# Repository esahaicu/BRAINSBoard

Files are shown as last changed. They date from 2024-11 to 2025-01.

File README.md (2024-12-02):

# BRAINSBoard

<p align="center">
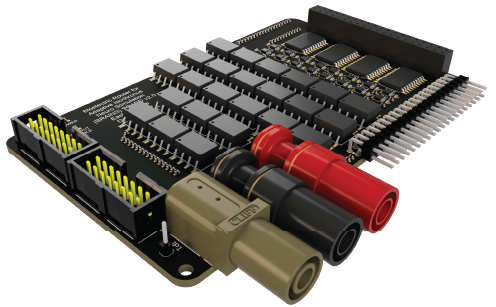
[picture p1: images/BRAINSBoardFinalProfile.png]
 
</p>

# Abstract

  **Objective:** Multipolar Intracranial Electrical Brain Stimulation (ICBS) is a promising method increasingly explored for use in both closed-loop neuromodulation experiments and clinical treatments for neurological diseases. Current tools for multipolar ICBS face several limitations that hinder exploratory research: high entry costs, lack of flexibility in managing different stimulation parameters and electrodes, absence of an open-source, customizable platform, and often an overabundance of features unnecessary for single-unit level exploratory research. These constraints limit the progress in understanding and applying multipolar ICBS effectively. To address these challenges, we developed the Bioelectric Router for Adaptive Isochronous Neuro Stimulation (BRAINS) Board.

  **Approach:** The BRAINS Board a cost-effective and customizable device designed to facilitate multipolar stimulation experiments across a 16-channel electrode array using common research electrode setups. The BRAINS Board interfaces with a microcontroller, allowing users to configure each channel for cathodal or anodal input, establish a grounded connection, or maintain a floating state. The design prioritizes ease of integration by leveraging standard tools like a microcontroller and an Analog Isolated Stimulator while providing options to customize setups according to experimental conditions. It also ensures output isolation, reduces noise, and supports remote configuration changes for rapid switching of electrode states. To test the efficacy of the board, there will be a series of tests run with 2 different stimulators with a fixed set of currents congruent with typical microcurrent brain stimulation. There will be 2 sets of bench tests: first with a direct connection to a DAQ system with current passing through 110KΩ resistors for all channels; next, a test through stimulation sent through contacts of a 16 channel electrode in saline and recordings through a Neuropixel. Once completed, monopolar, bipolar, and multipolar parameters will be tested in-vivo with stimulation and 3 Neuropixel recordings in V1.

  **Main Results:** The BRAINS Board, when delivering stimulation through a conventional isolated stimulator (A-M 4100), demonstrates no significant differences in Root Mean Square Error (RMSE) noise or signal-to-noise ratio compared to the baseline performance of the isolated stimulator alone. The board supports configuration changes at a rate of up to 600 Hz without introducing residual noise, enabling high-frequency switching necessary for temporally multiplexed multipolar stimulation.

  **Significance:** The BRAINS Board represents a significant advancement in exploratory brain stimulation research by providing a user-friendly, customizable, open source, and cost-effective tool capable of conducting sophisticated, reproducible, and finely controlled stimulation experiments. With its capacity for real-time information processing and efficient parameter exploration, the BRAINS Board is poised to enhance both exploratory research and clinical applications of closed-loop ICBS.

# Introduction

Intracranial electrical brain stimulation (EBS) is a cornerstone therapeutic approach in clinical neurology and neurosurgery, particularly for treating conditions like Parkinson's disease, obsessive compulsive disorder[1], [2], dystonia[3], and epilepsy[4]. Furthermore, microstimulation paradigms have been used for decades in animal research. Utilizing EBS with neural prosthetics has promise to improve the quality and efficacy of brain-machine interfaces[5]. Despite widespread clinical use and role in neuroscience research, our fundamental understanding of how EBS affects neural circuits remains surprisingly limited. Current clinical protocols rely heavily on trial-and-error programming approaches during and after electrode implantation stimulation parameters frequently require adjustment over multiple clinical visits to achieve optimal therapeutic effects [6], [7], [8].

While we know that EBS can activate varied neural elements - including somas, dendrites, and axons - the precise composition of recruited neural ensembles remains unclear[6], [7]. This knowledge gap is particularly evident in clinical settings, where stimulation parameters must often be modified empirically by clinicians during patient follow-up visits[8]. Recent advances in multipolar brain stimulation have shown promise [9] in providing more precise [10], [11] and efficient therapeutic outcomes [12]. Current FDA-approved devices typically offer unipolar, bipolar, and limited multipolar stimulation options (4-8 contacts), with clinicians generally exhausting unipolar configurations before exploring more complex stimulation patterns[6]. Research devices with more contacts....reference specific papers... However, investigating  advanced approaches, including multipolar stimulation, faces significant technical and practical barriers in most research settings. Traditional research tools for exploring multipolar stimulation, such as clinical neurostimulators or high-end research systems (e.g., Tucker-Davies STG5 Satellite, Intan headstages), are either prohibitively expensive, inflexible in their configuration, or excessive in their complexity for basic research applications [13].

The scientific community currently lacks access to flexible, open-source, cost-effective tools for exploring multipolar stimulation paradigms. Existing solutions often require substantial financial investment, offer limited customization options, and frequently include unnecessary features that complicate their use in fundamental research settings. These limitations have created a significant barrier to entry for researchers interested in exploring novel stimulation paradigms and understanding the basic principles of neural activation patterns.

To address these challenges, we developed a modular and readily reprogrammable interface - the Bioelectric Router for Adaptive Isochronous Neuro Stimulation (BRAINS) Board for control of electrical brain stimulation. This system enables rapid switching and multipolar stimulation while maintaining compatibility with existing monopolar and bipolar stimulation experimental frameworks. Our approach prioritizes accessibility, flexibility, and signal isolation while keeping costs aligned with standard experimental setups.   

# Hardware

The BRAINSBoard uses a custom designed PCB to ensure that:
 1) Output signal to the electrode array remains **isolated** with little to no leak or loss of current
 2) Channels can be set and changed **rapidly (~600Hz)**
 3) Channels can be controlled using any microcontroller and can be customizable

The BRAINSBoard is easy to plug into many up to 16-channel stimulation setups for experiments and can customizably recieve and communicate information to and from other devices in a setup. A current setup looks like:

<p align="center">
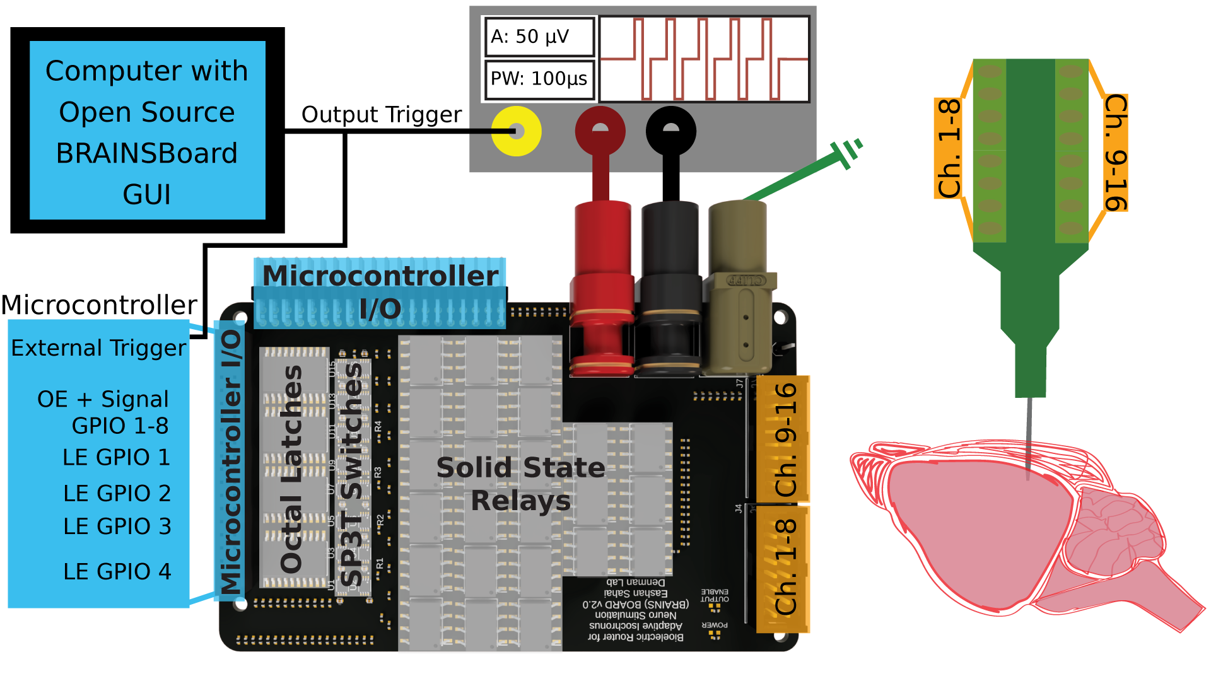
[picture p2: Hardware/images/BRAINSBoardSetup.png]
 
</p>

If you want to BUILD YOUR OWN:
Use the <a href="/Hardware/BRAINSBoard%20Production%20Files">following folder</a>, which has everything required to submit the PCB to a manufacturer to be processed.

For a more in-depth explanation of the schematic and setup of this board, <a href="/Hardware">look here</a>!

# Software

We have designed this to be compatible and easily programmed by any microcontroller. We have prewritten code to pair with an Arduino Pro Micro with the following configuration:

<p align="center">
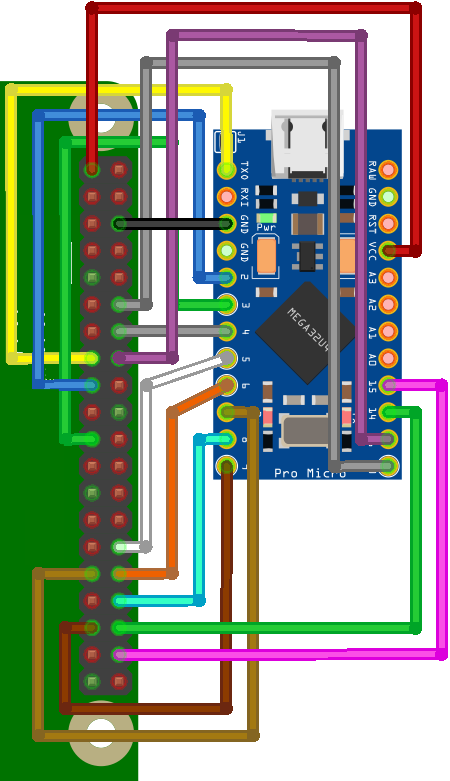
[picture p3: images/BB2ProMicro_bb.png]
 
</p>

Use the <a href="/Software/arduinoProMicroBRAINSBoard">following folder</a>, which has code that can be downloaded onto an Arduino Pro Micro.

The guide and description on how to easily control the board is <a href="/Software">here</a>!

# General Results

Hey! General results that will be good to prominently display as well as maybe setup pics could be great!

# Future Directions

Look forward <a href=https://github.com/esahaicu/BRAINSBoard/>HERE</a> for more updates on the BRAINSBoard that are based on, but not limited to, the following key improvements and a future timeline:

### By January 2025 - BRAINSBoard V3

1. Switching the <a href="https://cdn1-originals.webdamdb.com/14154_151801265?cache=1732603283&response-content-disposition=inline;filename=PAA193.pdf&response-content-type=application/pdf&Policy=eyJTdGF0ZW1lbnQiOlt7IlJlc291cmNlIjoiaHR0cCo6Ly9jZG4xLW9yaWdpbmFscy53ZWJkYW1kYi5jb20vMTQxNTRfMTUxODAxMjY1P2NhY2hlPTE3MzI2MDMyODMmcmVzcG9uc2UtY29udGVudC1kaXNwb3NpdGlvbj1pbmxpbmU7ZmlsZW5hbWU9UEFBMTkzLnBkZiZyZXNwb25zZS1jb250ZW50LXR5cGU9YXBwbGljYXRpb24vcGRmIiwiQ29uZGl0aW9uIjp7IkRhdGVMZXNzVGhhbiI6eyJBV1M6RXBvY2hUaW1lIjoyMTQ3NDE0NDAwfX19XX0_&Signature=KEhrRK-vYwk0ggFpEj8wrtBzJmtt7BLaQpuE0VpQ6zIkfrLoIbx35HtgxQp~mzP1G8wXjwMnEd2zExPyTWqPD8bcKLJTfQP483ssKtQgMZSv9g4kMZWmTeWzq72~uDpBGg3QDFOSoxpoQ4pNKS8JEbIiLR73WmyYWHy~x8HXiKn1oemtWMO5ZJkIW832eBlLtIbZF6mad9GiruNMyseB5M5vAtnD5xpdgm85AQOtLEowx-~A6fRC1GCmJKfGsC2NgjsDT588YpRlWTskNJhZ7zaYhGDO9GeALtxS0ZmNQy8JBUkahIwGCS4s0QiuV7Lvj7qD-rCDa4SswuSvqyvkgw__&Key-Pair-Id=APKAI2ASI2IOLRFF2RHA">current Solid State Relay</a> to a <a href="https://cdn1-originals.webdamdb.com/12956_135154079?cache=1729648393&response-content-disposition=inline;filename=OAA160.pdf&response-content-type=application/pdf&Policy=eyJTdGF0ZW1lbnQiOlt7IlJlc291cmNlIjoiaHR0cCo6Ly9jZG4xLW9yaWdpbmFscy53ZWJkYW1kYi5jb20vMTI5NTZfMTM1MTU0MDc5P2NhY2hlPTE3Mjk2NDgzOTMmcmVzcG9uc2UtY29udGVudC1kaXNwb3NpdGlvbj1pbmxpbmU7ZmlsZW5hbWU9T0FBMTYwLnBkZiZyZXNwb25zZS1jb250ZW50LXR5cGU9YXBwbGljYXRpb24vcGRmIiwiQ29uZGl0aW9uIjp7IkRhdGVMZXNzVGhhbiI6eyJBV1M6RXBvY2hUaW1lIjoyMTQ3NDE0NDAwfX19XX0_&Signature=AXHYEUwQeGlJv0wT-6YeKM1RikhenEa59iUFNI39tTOkFUg2SDUpqC-E0H8ncd0Q7HQ08yBqlckWgHi77eyu01f4YnqluGsyMgwveAA9lgVK35F8CKfdHTVbH9U3SGNk3P30u9mg-Cwjt3lLbItZ5srsjdkrtmY~ygdudVYNud--zzGRss3OerThwrDle2YjYWR0AnRQs9qA01ERjdj3iEWlwWsxjy~kbYyX732hxke7vOttaN5PPq~9jG1AofzusaQnYLKNld86RVlLb~SNYGWz9AfdbnLhnX-XlATFZXGDKhS-sPZHe1oXKVAZrJjDEzQASST77NQPldvNG~NaTg__&Key-Pair-Id=APKAI2ASI2IOLRFF2RHA">better Solid State Relay</a> for microstimulation with the current devices.
   - The current SSR has two key issues noted in this version 2 of the BRAINSBoard:
     - ***10µA leak current*** on the isolated channels that is solved in the <a href="https://github.com/esahaicu/BRAINSBoard/Results">results section </a> under issue #1 **vs** a ***250nA leak current*** in the newer Solid State Relay
     - ***50pF output capacitance*** on the isolated channels that is solved in the <a href="https://github.com/esahaicu/BRAINSBoard/Results">results section </a> under issue #1 **vs** a ***5pF leak current*** in the newer Solid State Relay
   - The goal is to remove a notable reduction in the signal provided due to leak and capacitance issues. Both a theoretical demonstration of the issue and intial results presenting the benefits of the new Solid State Relay based on saline tests in the <a href="https://github.com/esahaicu/BRAINSBoard/Results">results section</a> in the solution #1 Section
   - With this fix, we estimate only a 3% signal loss rather than estimated 30% loss of the signal current with high impedance electrodes.
2. Replace connector to any microcontroller with an embedded RP2040 microprocessor and develop the BRAINSBoard as the microcontroller itself to be able to implement more electrical isolation.
   - One noticeable issue (Problem #2) is that, when sending serial commands from a computer and through an Arduino where said computer is the power source for the board, there will be some introduced noise that is present in the LFP Band in Neuropixel recordings (though no noticeable noise in the AP Band of the recording) that is always present when a serial command is sent from the computer to the board.
   - We suspect this is due to ground loops forming between the building ground and the ground of the computer that is powering the Arduino
   - The most effective solution is to isolate the USB power, utilize an external power source, add sync and clock functionality, and allow for more customizability is by implementing a microprocessor like the RP2040.
3. Update Connectors:
   - USB and Power Connector Updates:
     - Since the plan is to embed a microprocessor directly onto the BRAINSBoard, we will utilize a USB-C connector directly on the board.
     - A 5.5mm DC Barrel Jack will also be added for external power.
   - Update the 2 2x8 Box Connctors to a more universal neuroscience connector with the NanoZ 2x<a href="(https://www.digikey.com/en/products/detail/samtec-inc/MOLC-110-01-S-Q/6695611)">32 Samtec Connector (MOLC‐110‐01‐S‐Q)</a>:
     - This will make it easier to connect to varying electrode headstages utilizing already shielded products like <a href="https://plexon.com/products/nanoz-adaptors-omnetics/#1585316524959-3f3aca9b-4d99">this one from Plexon</a>.
     - This also allows for easy modifications to upgrade the board to be compatible with 32 and 64 channel electrodes.
   - Omnetics18 Connector for a <a href="https://intantech.com/RHS_headstages.html?tabSelect=RHS16ch&yPos=0">16-Channel Recording Headstage</a>:
     - The plan is to implement more Solid State relays for a similar isolated input from the electrodes through the BRAINSBoard for a 16-channel recording headstage
     - The board will be setup to connect to the recording state instead of having a "floating" state as it does now when SP3T state is all LOW.
   - BNC Connectors along with male headers for microcontroller I/O
4. Update Hardware and Software Features:
   - Add in a full, standalone, downloadable control GUI for Mac, Windows, and Linux.
   - Work on setting up an Open-Ephys Plugin to work alongside the board.
   - Setup a physical screen and buttons to manually set up some features.

### Beyond BRAINSBoard V3

1. Create modular systems as follows:
   a. A base module that serves as a control center for all functions.
   b. Attachable 16-channel shields so that more channels can be added.
   c. Additional custom connectors to other common neuroscience tools (ie. recording devices, optogenetic tools, I/O breakouts, etc.)
2. FPGA compatibility to work towards closed-loop stimulation
3. Some system that allows for varying resistance over each channel to customize current sent to each individual electrode while still only requiring one Analog Isolated Stimulator. 

# REFERENCES
[1]	B. D. Greenberg et al., “Three-Year Outcomes in Deep Brain Stimulation for Highly Resistant Obsessive–Compulsive Disorder,” Neuropsychopharmacology, vol. 31, no. 11, pp. 2384–2393, Nov. 2006, doi: 10.1038/sj.npp.1301165.

[2]	T. Wichmann and M. R. DeLong, “Deep Brain Stimulation for Neurologic and Neuropsychiatric Disorders,” Neuron, vol. 52, no. 1, pp. 197–204, Oct. 2006, doi: 10.1016/j.neuron.2006.09.022.

[3]	“Electrical stimulation of the globus pallidus internus in patients with primary generalized dystonia: long-term results in: Journal of Neurosurgery Volume 101 Issue 2 (2004) Journals.” Accessed: Nov. 08, 2024. [Online]. Available: https://thejns.org/view/journals/j-neurosurg/101/2/article-p189.xml

[4]	C. N. Heck et al., “Two-year seizure reduction in adults with medically intractable partial onset epilepsy treated with responsive neurostimulation: Final results of the RNS System Pivotal trial,” Epilepsia, vol. 55, no. 3, p. 432, Feb. 2014, doi: 10.1111/epi.12534.

[5]	C. Orlemann, C. Boehler, R. Kooijmans, B. Li, M. Asplund, and P. Roelfsema, “Flexible Polymer Electrodes for Stable Prosthetic Visual Perception in Mice,” Adv. Healthc. Mater., vol. 13, p. e2304169, Mar. 2024, doi: 10.1002/adhm.202304169.

[6]	J. Vorwerk, A. A. Brock, D. N. Anderson, J. D. Rolston, and C. R. Butson, “A retrospective evaluation of automated optimization of deep brain stimulation parameters,” J. Neural Eng., vol. 16, no. 6, p. 064002, Nov. 2019, doi: 10.1088/1741-2552/ab35b1.

[7]	C. J. Hartmann, S. Fliegen, S. J. Groiss, L. Wojtecki, and A. Schnitzler, “An update on best practice of deep brain stimulation in Parkinson’s disease,” Ther. Adv. Neurol. Disord., vol. 12, p. 1756286419838096, 2019, doi: 10.1177/1756286419838096.

[8]	G. Deuschl et al., “Deep brain stimulation: postoperative issues,” Mov. Disord. Off. J. Mov. Disord. Soc., vol. 21 Suppl 14, pp. S219-237, Jun. 2006, doi: 10.1002/mds.20957.

[9]	J. Buhlmann, L. Hofmann, P. A. Tass, and C. Hauptmann, “Modeling of a Segmented Electrode for Desynchronizing Deep Brain Stimulation,” Front. Neuroengineering, vol. 4, Dec. 2011, doi: 10.3389/fneng.2011.00015.

[10]	D. N. Anderson et al., “The μDBS: Multiresolution, Directional Deep Brain Stimulation for Improved Targeting of Small Diameter Fibers,” Front. Neurosci., vol. 13, Oct. 2019, doi: 10.3389/fnins.2019.01152.

[11]	S. Zhang et al., “Comparing Current Steering Technologies for Directional Deep Brain Stimulation Using a Computational Model That Incorporates Heterogeneous Tissue Properties,” Neuromodulation, vol. 23, no. 4, p. 469, Aug. 2019, doi: 10.1111/ner.13031.

[12]	C. Pollo et al., “Directional deep brain stimulation: an intraoperative double-blind pilot study,” Brain, vol. 137, no. 7, pp. 2015–2026, Jul. 2014, doi: 10.1093/brain/awu102.

[13]	J. A. Frank, M.-J. Antonini, and P. Anikeeva, “Next-generation interfaces for studying neural function,” Nat. Biotechnol., vol. 37, no. 9, pp. 1013–1023, Sep. 2019, doi: 10.1038/s41587-019-0198-8.

## $\textbf{\color{white}This work was supported by NIH NINDS project number 1R01NS120850}$

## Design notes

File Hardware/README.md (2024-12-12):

# BRAINSBoard *HARDWARE*

<p align="center">
 
</p>

<p align="center">
<i>Illustrated Schematic of the BRAINSBoard</i>
</p>

## Purpose

The BRAINSBoard is a proprietary custom PCB that is designed to electronically switch between Cathode, Anode, Ground, and Floating states for 16 different electrode channels without physically interacting with the components during experiments. This enables:
- Stimulation at different loci in patterns.
- Grounding of every inactive pin to prevent noise.
- Use with a GUI designed for efficient pin switching during and between experiments.

## Components of the Board

The exact components are also all listed in the <a href="/Hardware/BRAINSBoard%20Production%20Files/BRAINSBoard_BOM.xlsx">Bill Of Materials</a> and can be produced using the Gerber and board files in the <a href="/Hardware/BRAINSBoard%20Production%20Files">BRAINSBoard Production Files Folder</a>

We will break down the components here with a general explanation of their benefits!

<p align="center">
 
</p>

## Connectors
- $\textbf{\color{yellow}Raspberry Pi/Arduino 2x20 Female Header}$ facilitates connections to control and process data from Arduino/Raspberry Pi. $\textbf{\color{yellow}2x20 90º Male Header}$ allows external connections to unused/useful pins
  - A Raspberry Pi 4B can be directly connected on top of the $\textbf{\color{yellow}2x20 Female Header}$. Connection Pinout as follows:

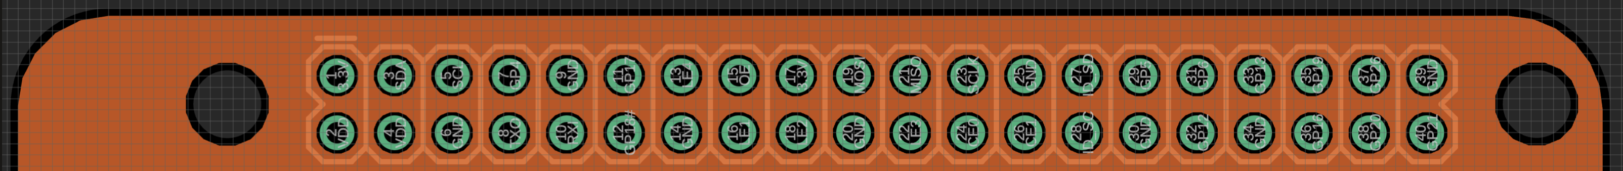
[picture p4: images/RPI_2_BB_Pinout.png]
Raspberry Pi to Brainsboard Connection

  - An Arduino can be connected to those same pins with the following Pinout (demonstrated with Arduino Pro Mini):
 
Arduino Pro Mini to Brainsboard Connection
  - Other tools (ie. sensors, actuators, external triggers) can be accessed from the $\textbf{\color{yellow}2x20 90º Male Header}$ with the following Pinout:

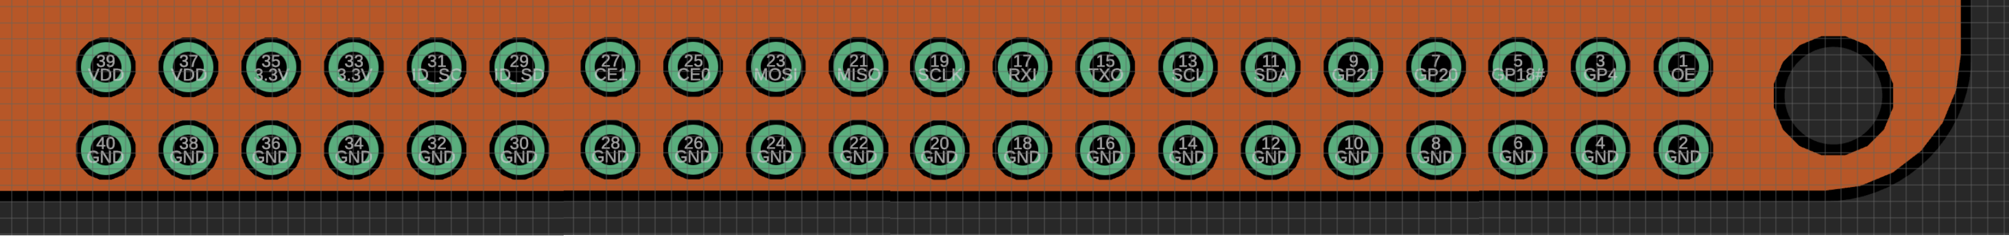
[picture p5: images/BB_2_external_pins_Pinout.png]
Brainsboard Connection to External Pins

- $\textbf{\color{white}NeuroNexus}$ Standard 2x8 Box Connectors with grounding on all top pins to minimize noise. Pinout:

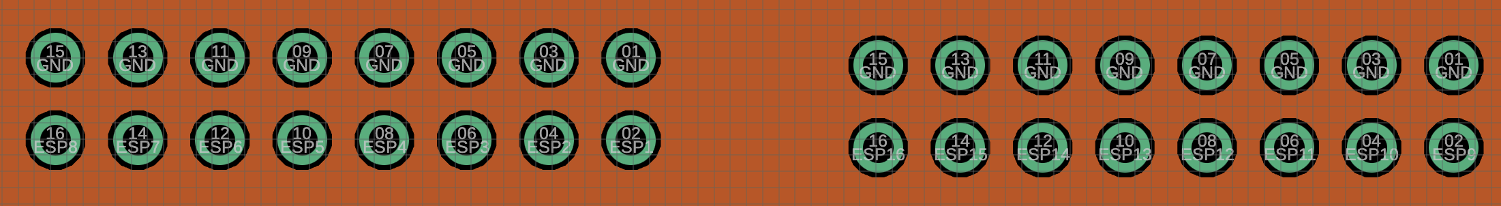
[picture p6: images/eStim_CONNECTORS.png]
Box Headers Pinout

- $\textbf{\color{red}Banana Connectors:}$ Connects to cathode and anode pulses from an Isolated Analog Power Stimulator (preferred A-M 4100) and a Signal Ground that can be connected to the same common ground as the electrode and stimulator.

## External Outputs:

$\textbf{\color{yellow}External Connectors:}$

[2x20 Female Header](https://www.digikey.com/en/products/detail/te-connectivity-amp-connectors/2-215307-0/1149668)

[2x20 90º Male Header](https://www.digikey.com/en/products/detail/oupiin/2011-2X20G00RB/13251482)

$\textbf{\color{white}Connectors to Neuronexus:}$

**Samtec Box Header** from [Digikey](https://www.digikey.com/en/products/detail/samtec-inc/TSS-108-01-G-D/2345166):

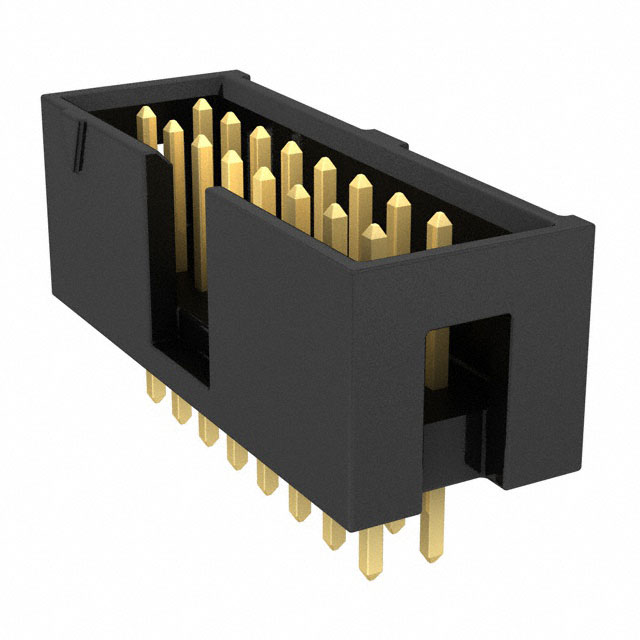
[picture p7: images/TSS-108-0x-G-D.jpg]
Box Header Example Image


$\textbf{\color{red}Connectors to Analog Stimulus Isolator:}$

[Ground Connector](https://www.digikey.com/en/products/detail/cliff-electronic-components-ltd/FCR7350G/17729033)

[Cathode Stimulus Connector](https://www.digikey.com/en/products/detail/pomona-electronics/73099-2/10483465)

[Anode Stimulus Connector](https://www.digikey.com/en/products/detail/pomona-electronics/73099-0/10483460)

## Electronics for Selecting Channels:

The following are used to be able to utilize Arduino Logic and rapidly change the connection between our stimulus signal from the isolated stimulator and the respective electrode channels.

### $\textbf{\color{#FF69B4}Octal Transparent D-Type Latch}$
- Requires a VCC +5V and ground.
- Output Enable and Latch Enable controls, connected to Arduino/Raspberry Pi, to manage pin outputs.
- Utilizes multiplexing capabilities to reduce connections needed to the microcontronoller and allows for future scalability.
- Latch capabilities ensure channel selection stability until change is required.
- [Texas Instruments Octal Transparent D-Type Latch](https://www.digikey.com/en/products/detail/texas-instruments/CY74FCT373TSOC/1508737)

### $\textbf{\color{orange}Analog SP3T Switch}$
- Two inputs determine the current path (cathode, anode, ground, or floating).
- Output directed through a connector managing pin outputs.
- Useful digital switch to ensure one of the four output states is set at all times.
- [Texas Instruments Analog SP3T Switch](https://www.digikey.com/en/products/detail/texas-instruments/TS5A3357DCUR/695801)

### $\textbf{\color{cyan}Solid State Relay}$
- Activated by a control switch, it powers an LED internally, which in turn activates a photosensitive diode to close the circuit.
- Optical Isolation prevents electrical interference from the microcontroller side of the circuit to the Analog Isolator stimulus sent to the respective channels.
- These specific Solid State Relays will be useful in handling high variance in Volatge due to unpredictable resistance in the brain as current stimulus is sent.
- [IXYS 600V 100mA Dual Single Pole Normally Open Relay](https://www.digikey.com/en/products/detail/ixys-integrated-circuits-division/PAA193STR/3077694)

### $\textbf{\color{green}LEDS}$
- Top LED is a $\text{\color{red}RED LED}$ that is utilized to indicate whether or not the BRAINS Board is receiving power.
- Bottom LED is a $\text{\color{green}GREEN LED}$ that is utilized to indicate whether the Output Enable is activated, determining whether or not outputs are being sent to change channels

## $\textbf{\color{white}This work was supported by NIH NINDS project number 1R01NS120850}$

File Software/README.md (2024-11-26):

# BRAINSBoard *Software*

## BRAINS BOARD SPECIFIC SOFTWARE

There are various sets of code designed to interface with the BRAINS Board through either the Arduino or Raspberry Pi.
These are guides on how they are designed as well as a simple measure as to how they may be manipulated for various uses.

### PART 1: Using Serial Communication with Arduino to Map Channels:

The current BRAINS Board API is built around Serial Inputs that are translated into pin activation using the [Brainsboard Serial Program Arduino Code](brainsboard_serial_pgm.ino)

This is also all right now designed to be used alongside an Arduino Micro Pro with the pinout shown below, though it can easily be changed to work with any Arduino board and pinout using the #define functions.

<p align="center">

</p>

The following pins correspond to channels above:
| Electrode Channel |    Arduino Pins     |
|:-----------------:|:-------------------:|
| Channel **1**     | Pin 16 + 1 + 5 + 6  |
| Channel **2**     | Pin 16 + 1 + 7 + 8  |
| Channel **3**     | Pin 16 + 1 + 9 + 10 |
| Channel **4**     | Pin 16 + 1 + 14 + 15|
| Channel **5**     | Pin 16 + 2 + 5 + 6  |
| Channel **6**     | Pin 16 + 2 + 7 + 8  |
| Channel **7**     | Pin 16 + 2 + 9 + 10 |
| Channel **8**     | Pin 16 + 2 + 14 + 15|
| Channel **9**     | Pin 16 + 3 + 5 + 6  |
| Channel **10**    | Pin 16 + 3 + 7 + 8  |
| Channel **11**    | Pin 16 + 3 + 9 + 10 |
| Channel **12**    | Pin 16 + 3 + 14 + 15|
| Channel **13**    | Pin 16 + 4 + 5 + 6  |
| Channel **14**    | Pin 16 + 4 + 7 + 8  |
| Channel **15**    | Pin 16 + 4 + 9 + 10 |
| Channel **16**    | Pin 16 + 4 + 14 + 15|

**The logic is this way because of the following:**

<p align="center">

</p>

- Our **Output Enable** pin, that is connected to all 4 of the Octal Latches, is connected to **Arduino Pin 16**
- We have 4 **Latch Enable** pins that are used to determine which latch we are controlling
  - **Pin 1** is connected to the first **OCTAL LATCH**, which controls signals sent to the **SP3T** switches that set channel configuration for **Electrode Channels 1-4**
  - **Pin 2** is connected to the second **OCTAL LATCH**, which controls signals sent to the **SP3T** switches that set channel configuration for **Electrode Channels 5-8**
  - **Pin 3** is connected to the third **OCTAL LATCH**, which controls signals sent to the **SP3T** switches that set channel configuration for **Electrode Channels 9-12**
  - **Pin 4** is connected to the fourth **OCTAL LATCH**, which controls signals sent to the **SP3T** switches that set channel configuration for **Electrode Channels 13-16**
- We then have **8 Data Input** pins connected to all of the **Octal Latches**, which will change the state of the digital output of the latches to High or Low dependent on a) if the latch enable for said Octal Latch is on and b) if the Arduino pin connected to each digital input pin is high or low
  - **Pins 5 and 6** control the output to the **SP3T** controlling **Electrode Channels 1, 5, 9, and 13**.
  - **Pins 7 and 8** control the output to the **SP3T** controlling **Electrode Channels 2, 6, 10, and 14**.
  - **Pins 9 and 10** control the output to the **SP3T** controlling **Electrode Channels 3, 7, 11, and 15**.
  - **Pins 14 and 15** control the output to the **SP3T** controlling **Electrode Channels 4, 8, 12, and 16**.

**Important Note:** The **A0 pin** is used as an input of any External Triggers from any other device (ie. a stimulator) for the board to use as an input to switch channels, if required.

The code also has 4 states that any channel can be set to at any given moment: **FLOATING**, **CATHODE**, **ANODE**, and **SIGNAL GROUND**. The board is designed to allow the **OCTAL LATCH** to send 2 outputs to any given **SP3T** correlated to a specific electrode channel, and logic of the switch by the **SP3T** is treated as follows:
| INPUT 1 STATE | INPUT 2 STATE | CHANNEL CONNECTED |
|:-------------:|:-------------:|:-----------------:|
| **LOW**       | **LOW**       | **FLOATING**      |
| **HIGH**      | **LOW**       | **CATHODE**       |
| **LOW**       | **HIGH**      | **ANODE**         |
| **HIGH**      | **HIGH**      | **SIGNAL GROUND** |

**Important Note:** The **SIGNAL GROUND** is connecting any signal connected to the $\textbf{\color{green}Green Banana Connector}$, which should ideally connected to the same **Reference Ground** that you would use for any electrophysiology or stimulation experiment.

### Serial Communication Logic:

<p align="center">

</p>

**The following is a step-by-step guide for utilizing any serial communication to control the channel outputs at any given time**
1. Ensure you are using 115200 bps as the data rate for for Serial line
2. '[' Begins reading channel Data
3. **'{X1}'** is a *Hexadecimal Number*
    - **To Set Channels 1-10:** X1 corresponds to a numerical value Channel # - 1 (ie. Channel 1 is 0, Channel 2 is 1, ..., Channel 10 is 9)
    - **To Set Channels 11-16:** X1 corresponds to an alphabtical value between A-F (ie. Channel 11 is A, Channel 12 is B, ..., Channel 16 is F)
4. **'{X2}'** is a *Character*
      - **F** for **FLOATING**
      - **C** for **CATHODE**
      - **A** for **ANODE**
      - **G** for **SIGNAL GROUND**
5. **']'** Closes *Reading Channel States* and *"Applies"* the channel states by utilizing logic to change where channels are connected
6. **'x'** Sets a *wait* until the **External Trigger Pin** recieves a signal (and won't continue until that trigger is low to change anything)
7. **'{t}{u}'** Sets a *wait* for a set time
      - **'{t}'** is a *numerical value* that is read and stored until the serial code reads a non-numerical value
      - **'{u}'** is a *character* that is written after the numerical values have been written that determines the units of delay time
        - **s** will set the *time {t}* to seconds
        - **m** will set the *time {t}* to milliseconds
        - **u** will set the *time {t}* to microseconds
8. **'l{c}'** Sets up a *loop* for the inputted channel setups for *{c}* more counts
      - If *{c}* is not set, it will infinitely loop.
9. **Important Note:** It is not necessary to write out every channel, previous channel states are already stored and latched until that specific channel is changed
##### Example Serial Command:
**[0F1F2F3F4F5F6F7F8F9FAFBFCFDFEFFF]200u[0C1A]x[0G1GEAFC]2sl3**
- This will first **set every channel** to **FLOATING**
- It will then **wait 200 microseconds**
- It will then change **Channel 1** to **CATHODE** and **Channel 2** to **ANODE**
- It will then **wait** until it recieves the **External Trigger** at **Pin A0**
- It will then change **Channel 1** and **Channel 2** to **SIGNAL GROUND** and **Channel 15** to **ANODE** and **Channel 16** to **CATHODE**
- It will then **wait 2 seconds**
- It then reads **l3**, so it will **loop** the previous steps **3 more times**

### PART 2: Using the Raspberry Pi to Map Channels Directly

The BRAINS Board was initially designed to directly integrate the various connections on a Raspberry Pi to map pins to channels and work harmoniously as a modular device that can work alongside other tools in an experimental setting. There are both benefits and drawbacks to using this microcontroller over an Arduino, laid out as follows:
#### BENEFITS:
1. BRAINS Board easily snaps into a Raspberry Pi, no external connection is needed
2. Any pins not used to directly control the logic of the BRAINS Board can be easily accessed through the side male pins, following the pinout shown here:

<p align="center">

</p>

3. Doesn't rely on Serial Communication to switch pinout, which can reduce latency
4. Allows for communication over WiFi which allows for non-wired control to directly switch channels
**When Using This Microcontroller Is Better:** The ideal use for the Raspberry Pi over an Arduino is when you are just reading an external signal or series of them and want to create a closed loop transition between channels based on multiple complicated inputs feeding directly into the Raspberry Pi, given that those inputs are able to be read by the Linux system and processed that way, **OR** when latency isn't very important but non-wired communication is essential or easier. 
#### DRAWBACKS:
1. Raspberry Pi uses CPU for running Debian, can create unwanted latency due to other processes running
2. Latency of WiFi communication relatively high
3. Serial read latency of Raspberry Pi is higher than Arduino Serial read latency
4. Debian (Linux) software won't run various softwares (many stimulator softwares are written specifically for Windows computer)
**When Using This Microcontroller is Not Optimal:** The Arduino controller is better when running integrated software with other devices that need a computer to process the information or program other things at the same time (ie. the STG5 Isolated Analog Stimulator, a MultiChannelSystems product that can only be customizably programmed on a Windows using their .dll Package for Windows) **OR** if latency based on external readings is critical and the processing can't be done on a Raspberry Pi (ie. if there were a developed closed-loop system based on the readings of inserted Neuropixels real-time to manipulate activated channels in a closed-loop system).

With that said, there are only a few changes in terms of the pinout when programming as such, all already established with the [GPIO](GPIO.py) script already set. The connections to the BRAINS Board from GPIO pins on the Raspberry Pi are as follows:

| PIN ON BRAINS BOARD | GPIO PIN ON RASPBERRY PI |
|:-------------------:|:------------------------:|
|**OE PIN**           | 22                       |
|**LE PIN 1**         | 23                       |
|**LE PIN 2**         | 24                       |
|**LE PIN 3**         | 25                       |
|**LE PIN 4**         | 27                       |
|**DIGITAL INPUT 1**  | 5                        |
|**DIGITAL INPUT 2**  | 6                        |
|**DIGITAL INPUT 3**  | 12                       |
|**DIGITAL INPUT 4**  | 13                       |
|**DIGITAL INPUT 5**  | 16                       |
|**DIGITAL INPUT 6**  | 17                       |
|**DIGITAL INPUT 7**  | 19                       |
|**DIGITAL INPUT 8**  | 26                       |

The GPIO code uses these and just takes 16 individual strings as channel_state = [...] with **F** for **FLOATING**, **C** for **CATHODE**, **A** for **ANODE**, and **G** for **SIGNAL GROUND** and the delay can be set using the precise_sleep function. Use general Python functionality to be able to program this any which way.

## $\textbf{\color{white}This work was supported by NIH NINDS project number 1R01NS120850}$

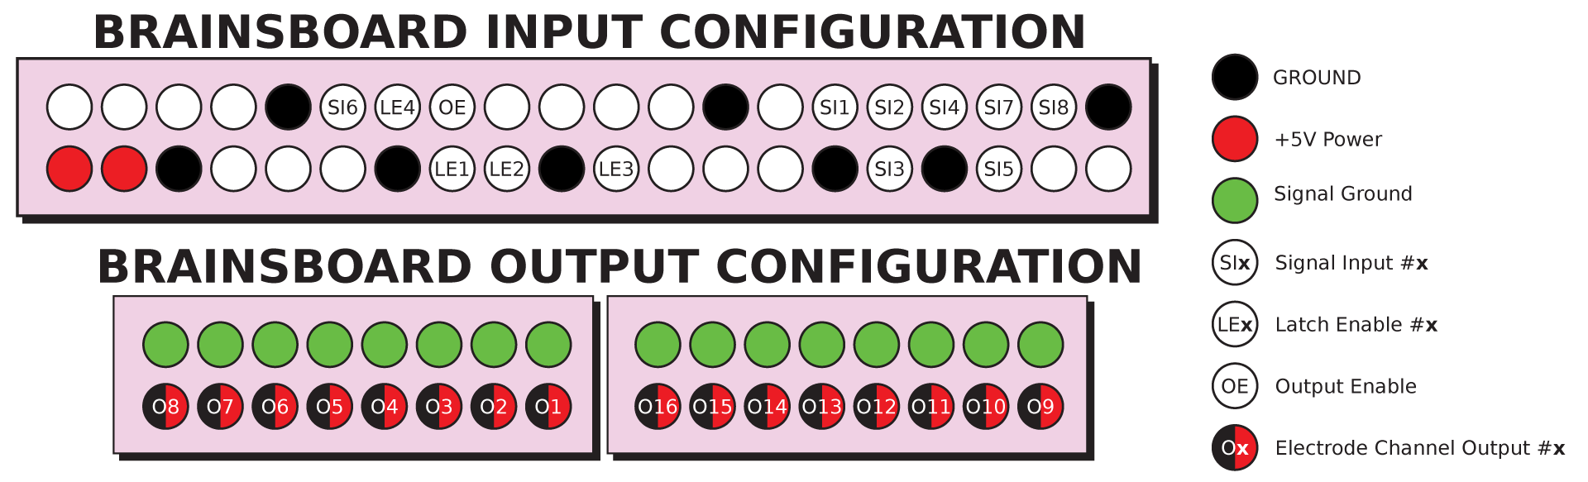
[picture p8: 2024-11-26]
Software/images/pinoutConfig.png

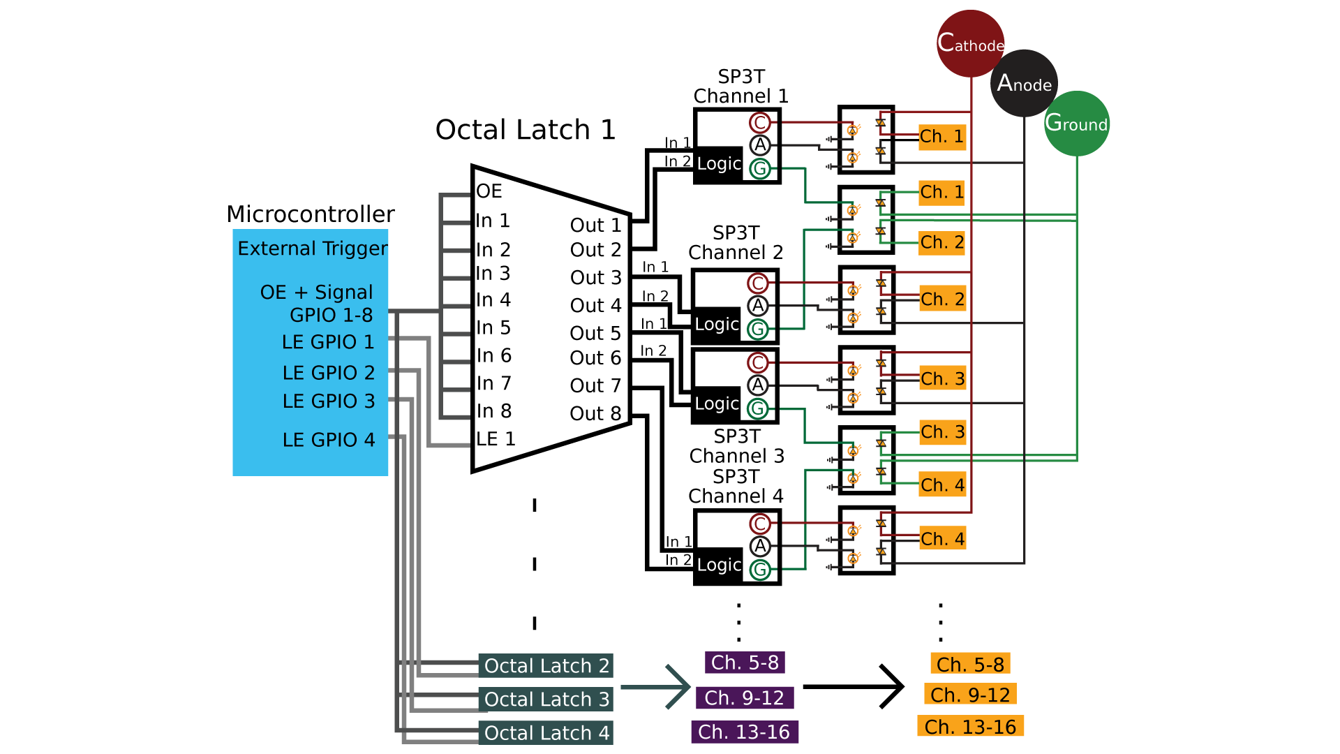
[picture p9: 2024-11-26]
Hardware/images/BRAINSBoardSchematic.png

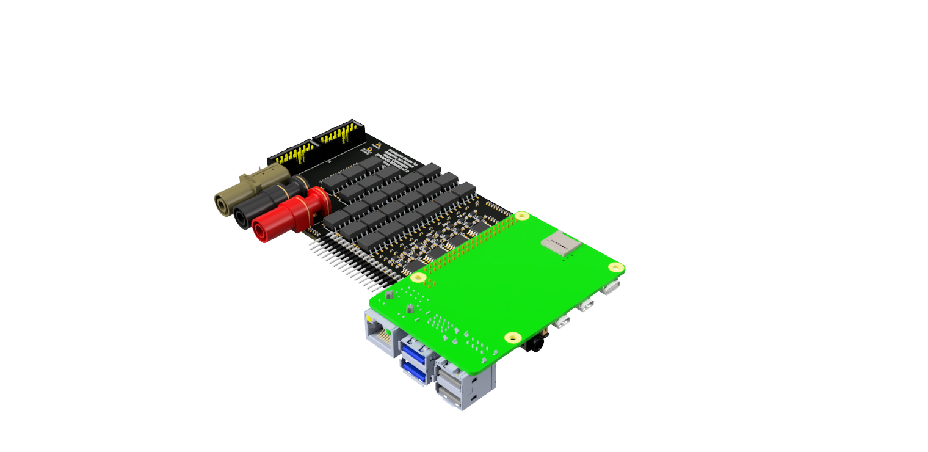
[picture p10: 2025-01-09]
images/bb_wpi.PNG

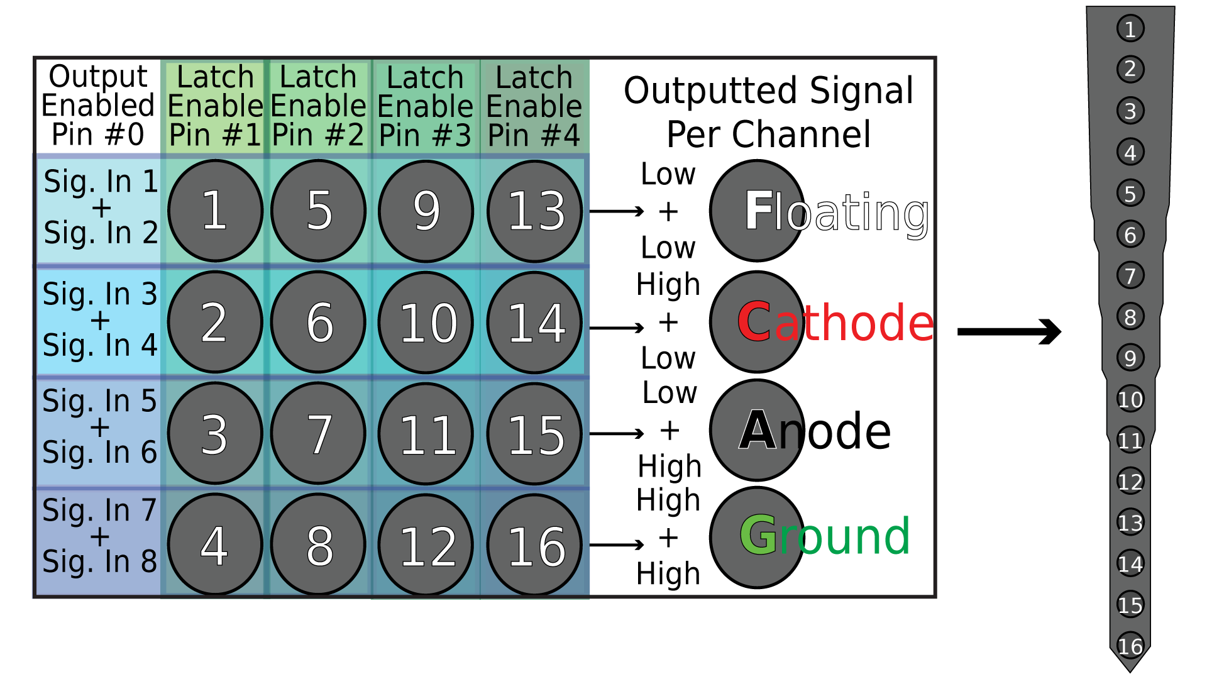
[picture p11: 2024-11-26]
Software/images/signalDemo.png

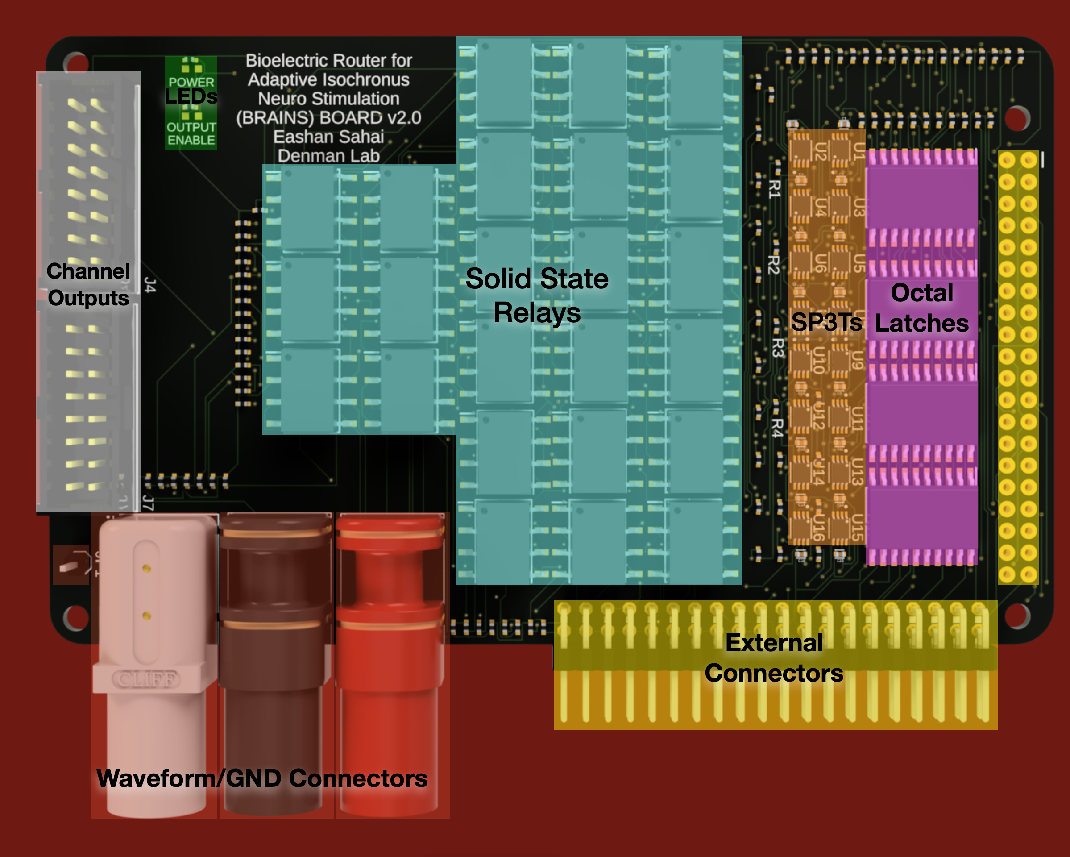
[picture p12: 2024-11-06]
images/BRAINSBoard_Top_Labelled.png

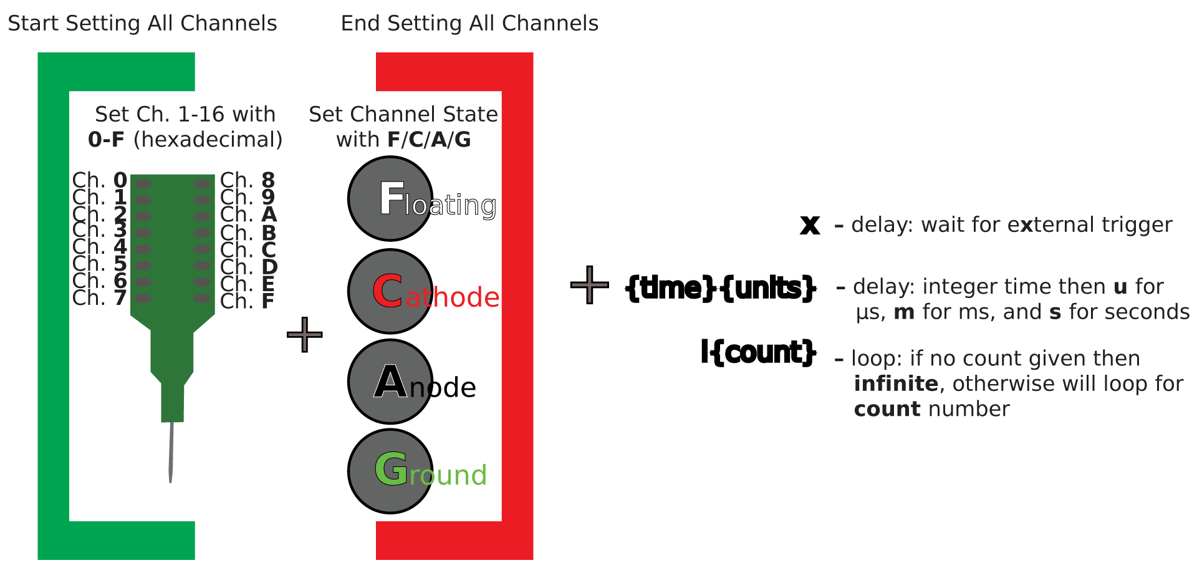
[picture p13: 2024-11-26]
Software/images/serialCommandDemo.png

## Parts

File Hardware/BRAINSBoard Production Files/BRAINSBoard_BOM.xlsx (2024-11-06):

Comment | Designator | Footprint
1K | R1, R2, R3, R4, R6, R7, R8, R9, R10, R11, R12, R13, R14, R15, R16, R17, R18, R19, R20, R21, R22, R23, R24, R25, R26, R27, R28, R29, R30, R31, R32, R33, R34, R35, R36, R37, R38, R39, R40, R41, R42, R43, R44, R45, R46, R47, R48, R49, R50, R51, R52, R53, R54, R55, R56, R57, R58, R59, R60, R61, R62, R63, R64, R65, R66, R67, R68, R69, R70, R71, R72, R73, R74, R75, R76, R77, R78, R79, R80, R81, R82, R83, R84, R85, R86, R87 | RC0402JR-071KL
73099-0 | J5 | 730990
73099-2 | J6 | 730990
CL05A104KA5NNNC | C1, C2, C3, C4, C5, C6, C7, C8, C9, C10, C11, C12, C13, C14, C15, C16 | CAPC1005X55N
PAA193STR | IC5, IC6, IC7, IC8, IC9, IC10, IC11, IC12, IC13, IC14, IC15, IC16, IC17, IC18, IC19, IC20, IC21, IC22, IC23, IC24, IC25, IC26, IC27, IC28 | SOP254P952X457-8N
PINHD-1X1 | JP1 | 1X01
2-215307-0 | J3 | 2X20
CY74FCT373TSOC | IC1, IC2, IC3, IC4 | SOIC127P1030X265-20N
TS5A3357DCUR | U1, U2, U3, U4, U5, U6, U7, U8, U9, U10, U11, U12, U13, U14, U15, U16 | SOP50P310X90-8N
TSS-108-01-G-D-LL | J4, J7 | SAMTEC_TSS-108-01-G-D-LL
4654-FCR7350G-ND | J2 | CONN_FCR7350G_CLF
LTST-C191KGKT | OUTPUT ENABLE | 0603 SMD/LED_LTST-C190CKT_LTO
LTST-C191KRKT | POWER | 0603 SMD/LED_LTST-C190CKT_LTO
2011-2X20G00RB | JP4 | 2X20/90

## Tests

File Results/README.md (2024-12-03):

# BRAINSBoard Results

<p align="center">
 
</p>

## Key Elements of the BRAINSBoard:
### 1. Analog Stimulus Isolation

<p align="center">
 
</p>

<p align="center">
 
</p>

#### Problem 1: Leak Current and Output Capacitance

 -
#### Solution 1: Replace the <a href="https://cdn1-originals.webdamdb.com/14154_151801265?cache=1732603283&response-content-disposition=inline;filename=PAA193.pdf&response-content-type=application/pdf&Policy=eyJTdGF0ZW1lbnQiOlt7IlJlc291cmNlIjoiaHR0cCo6Ly9jZG4xLW9yaWdpbmFscy53ZWJkYW1kYi5jb20vMTQxNTRfMTUxODAxMjY1P2NhY2hlPTE3MzI2MDMyODMmcmVzcG9uc2UtY29udGVudC1kaXNwb3NpdGlvbj1pbmxpbmU7ZmlsZW5hbWU9UEFBMTkzLnBkZiZyZXNwb25zZS1jb250ZW50LXR5cGU9YXBwbGljYXRpb24vcGRmIiwiQ29uZGl0aW9uIjp7IkRhdGVMZXNzVGhhbiI6eyJBV1M6RXBvY2hUaW1lIjoyMTQ3NDE0NDAwfX19XX0_&Signature=KEhrRK-vYwk0ggFpEj8wrtBzJmtt7BLaQpuE0VpQ6zIkfrLoIbx35HtgxQp~mzP1G8wXjwMnEd2zExPyTWqPD8bcKLJTfQP483ssKtQgMZSv9g4kMZWmTeWzq72~uDpBGg3QDFOSoxpoQ4pNKS8JEbIiLR73WmyYWHy~x8HXiKn1oemtWMO5ZJkIW832eBlLtIbZF6mad9GiruNMyseB5M5vAtnD5xpdgm85AQOtLEowx-~A6fRC1GCmJKfGsC2NgjsDT588YpRlWTskNJhZ7zaYhGDO9GeALtxS0ZmNQy8JBUkahIwGCS4s0QiuV7Lvj7qD-rCDa4SswuSvqyvkgw__&Key-Pair-Id=APKAI2ASI2IOLRFF2RHA">PAA193 SSR</a> with <a href="https://cdn1-originals.webdamdb.com/12956_135154079?cache=1729648393&response-content-disposition=inline;filename=OAA160.pdf&response-content-type=application/pdf&Policy=eyJTdGF0ZW1lbnQiOlt7IlJlc291cmNlIjoiaHR0cCo6Ly9jZG4xLW9yaWdpbmFscy53ZWJkYW1kYi5jb20vMTI5NTZfMTM1MTU0MDc5P2NhY2hlPTE3Mjk2NDgzOTMmcmVzcG9uc2UtY29udGVudC1kaXNwb3NpdGlvbj1pbmxpbmU7ZmlsZW5hbWU9T0FBMTYwLnBkZiZyZXNwb25zZS1jb250ZW50LXR5cGU9YXBwbGljYXRpb24vcGRmIiwiQ29uZGl0aW9uIjp7IkRhdGVMZXNzVGhhbiI6eyJBV1M6RXBvY2hUaW1lIjoyMTQ3NDE0NDAwfX19XX0_&Signature=AXHYEUwQeGlJv0wT-6YeKM1RikhenEa59iUFNI39tTOkFUg2SDUpqC-E0H8ncd0Q7HQ08yBqlckWgHi77eyu01f4YnqluGsyMgwveAA9lgVK35F8CKfdHTVbH9U3SGNk3P30u9mg-Cwjt3lLbItZ5srsjdkrtmY~ygdudVYNud--zzGRss3OerThwrDle2YjYWR0AnRQs9qA01ERjdj3iEWlwWsxjy~kbYyX732hxke7vOttaN5PPq~9jG1AofzusaQnYLKNld86RVlLb~SNYGWz9AfdbnLhnX-XlATFZXGDKhS-sPZHe1oXKVAZrJjDEzQASST77NQPldvNG~NaTg__&Key-Pair-Id=APKAI2ASI2IOLRFF2RHA">OAA160 SSR</a>

### 2. Rapid and Customizable Switching and Configurations of electrode contacts

<p align="center">
 
</p>

***(a):*** *tested average of stimulation at various frequencies to determine the maximum frequency one could switch between channels with a direct connection to a NIDAQ recording at 30MHz. The board was able to adequately switch between configurations that involved switching states of every pin from an active cathode-anode pairing to a ground state in clusters of four without leak due to Solid State Relay or Octal Latch Reconfiguration or On/Off times at ~ 600Hz.* ***(b):*** *switching times will increase for every new Octal Latch (1 for every 4 channels) required to set state configurations for electrode channels. Recorded duration of the Output Enable on the NIDAQ at 30MHz demonstrates that for one Octal Latch, activation time is between 133* $\tfrac{1}{3}\$ *μs to 166* $\tfrac{2}{3}$ *μs and each additional Octal Latch adds ~ 66* $\tfrac{2}{3}\$ *μs to set channel states on the side of the Arduino Pro Micro. Precise measurement of time taken is limited by the 30MHz sample rate* ***(c):*** *recording of Multichannel Monopolar 50µA Cathode Leading 500µs Biphasic Single Pulses rapidly switching active cathode channels at 500 Hz. Stimulation sent through an A-M 4100 Analog Isolated Stimulator through the BRAINSBoard with all 16 outputs connected through a 100kΩ resistor to a NIDAQ Board and a building ground. No leak current presents itself when every other channel is grounded and a single contact is activated.* ***(d):*** *attempted multipolar test with a single cathode and multiple anode channels in saline with 50µA Cathode Leading 500µs Biphasic Single Pulses with an AM4100 Analog Isolated Stimulator through the BRAINSBoard to a NeuroNexus A1x16 (50 µm spacing between contacts) Electrode Array.*

**Rapid switching has the following theoretical time limitations due to board components beyond the Solid State Relays:**
<p align="center">
 
</p>

*** *denotes dependancy on software efficiency and specific microcontroller used* 

#### Problem 2: LFP spike when Serial Commands sent
 - Put in a pic of noise from a recording?
#### Solution 2: USB Isolation
 - Talk about how it's done?

### 3. Programmability:

## $\textbf{\color{white}This work was supported by NIH NINDS project number 1R01NS120850}$

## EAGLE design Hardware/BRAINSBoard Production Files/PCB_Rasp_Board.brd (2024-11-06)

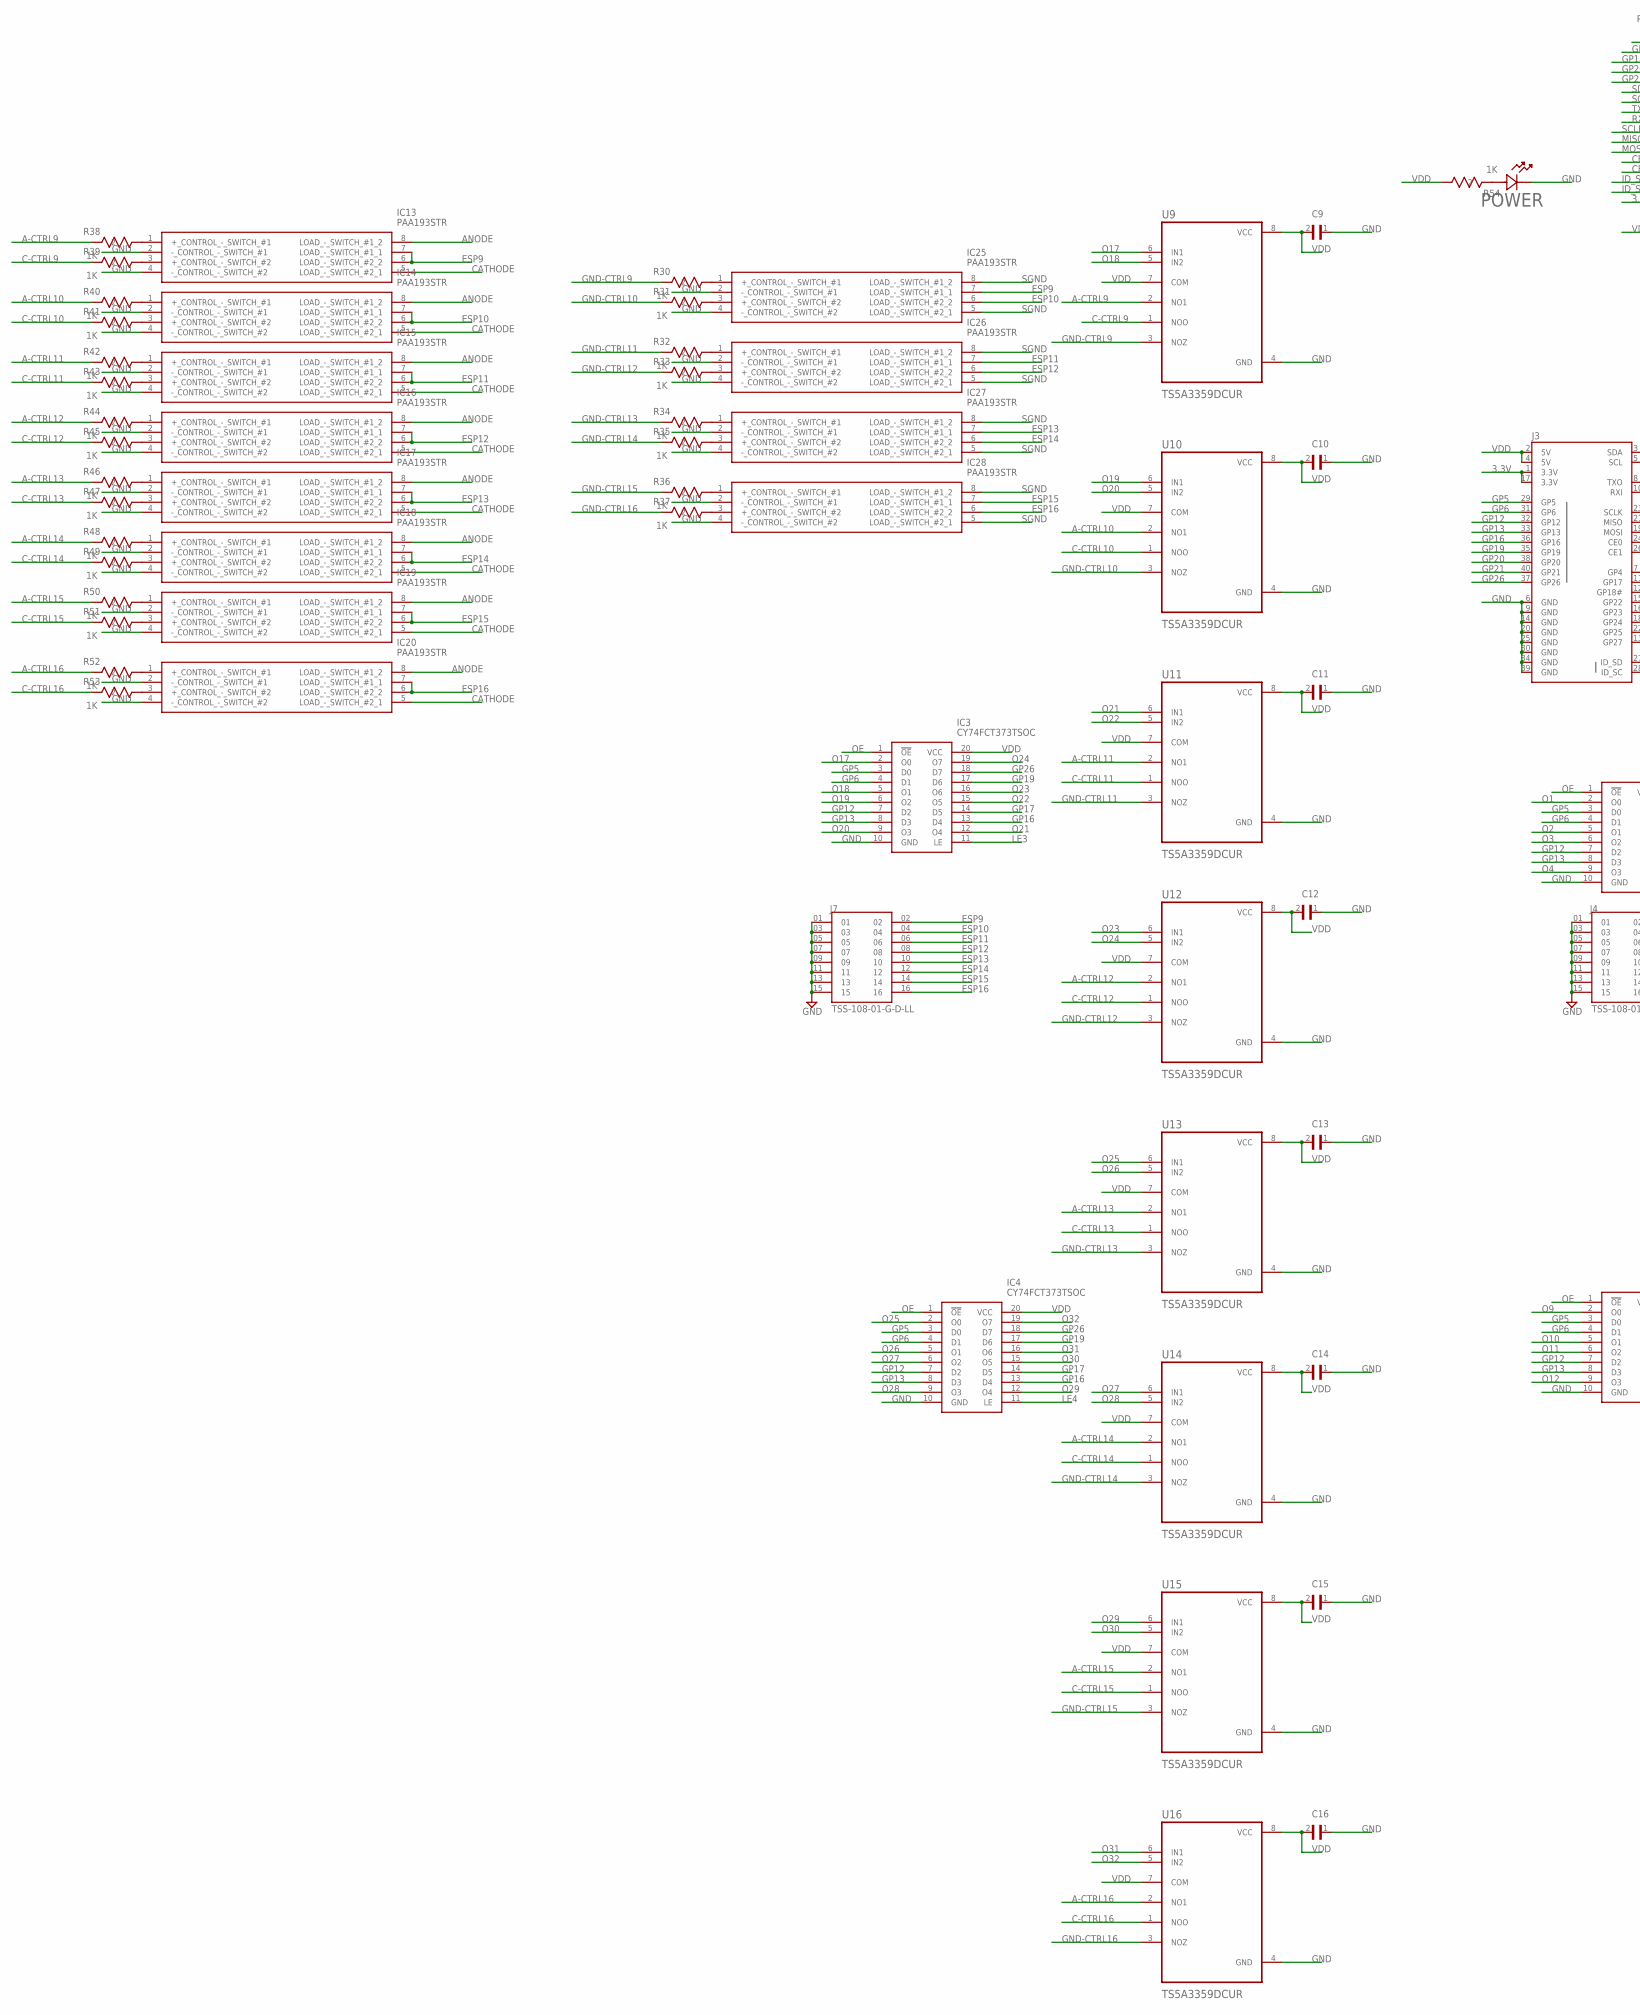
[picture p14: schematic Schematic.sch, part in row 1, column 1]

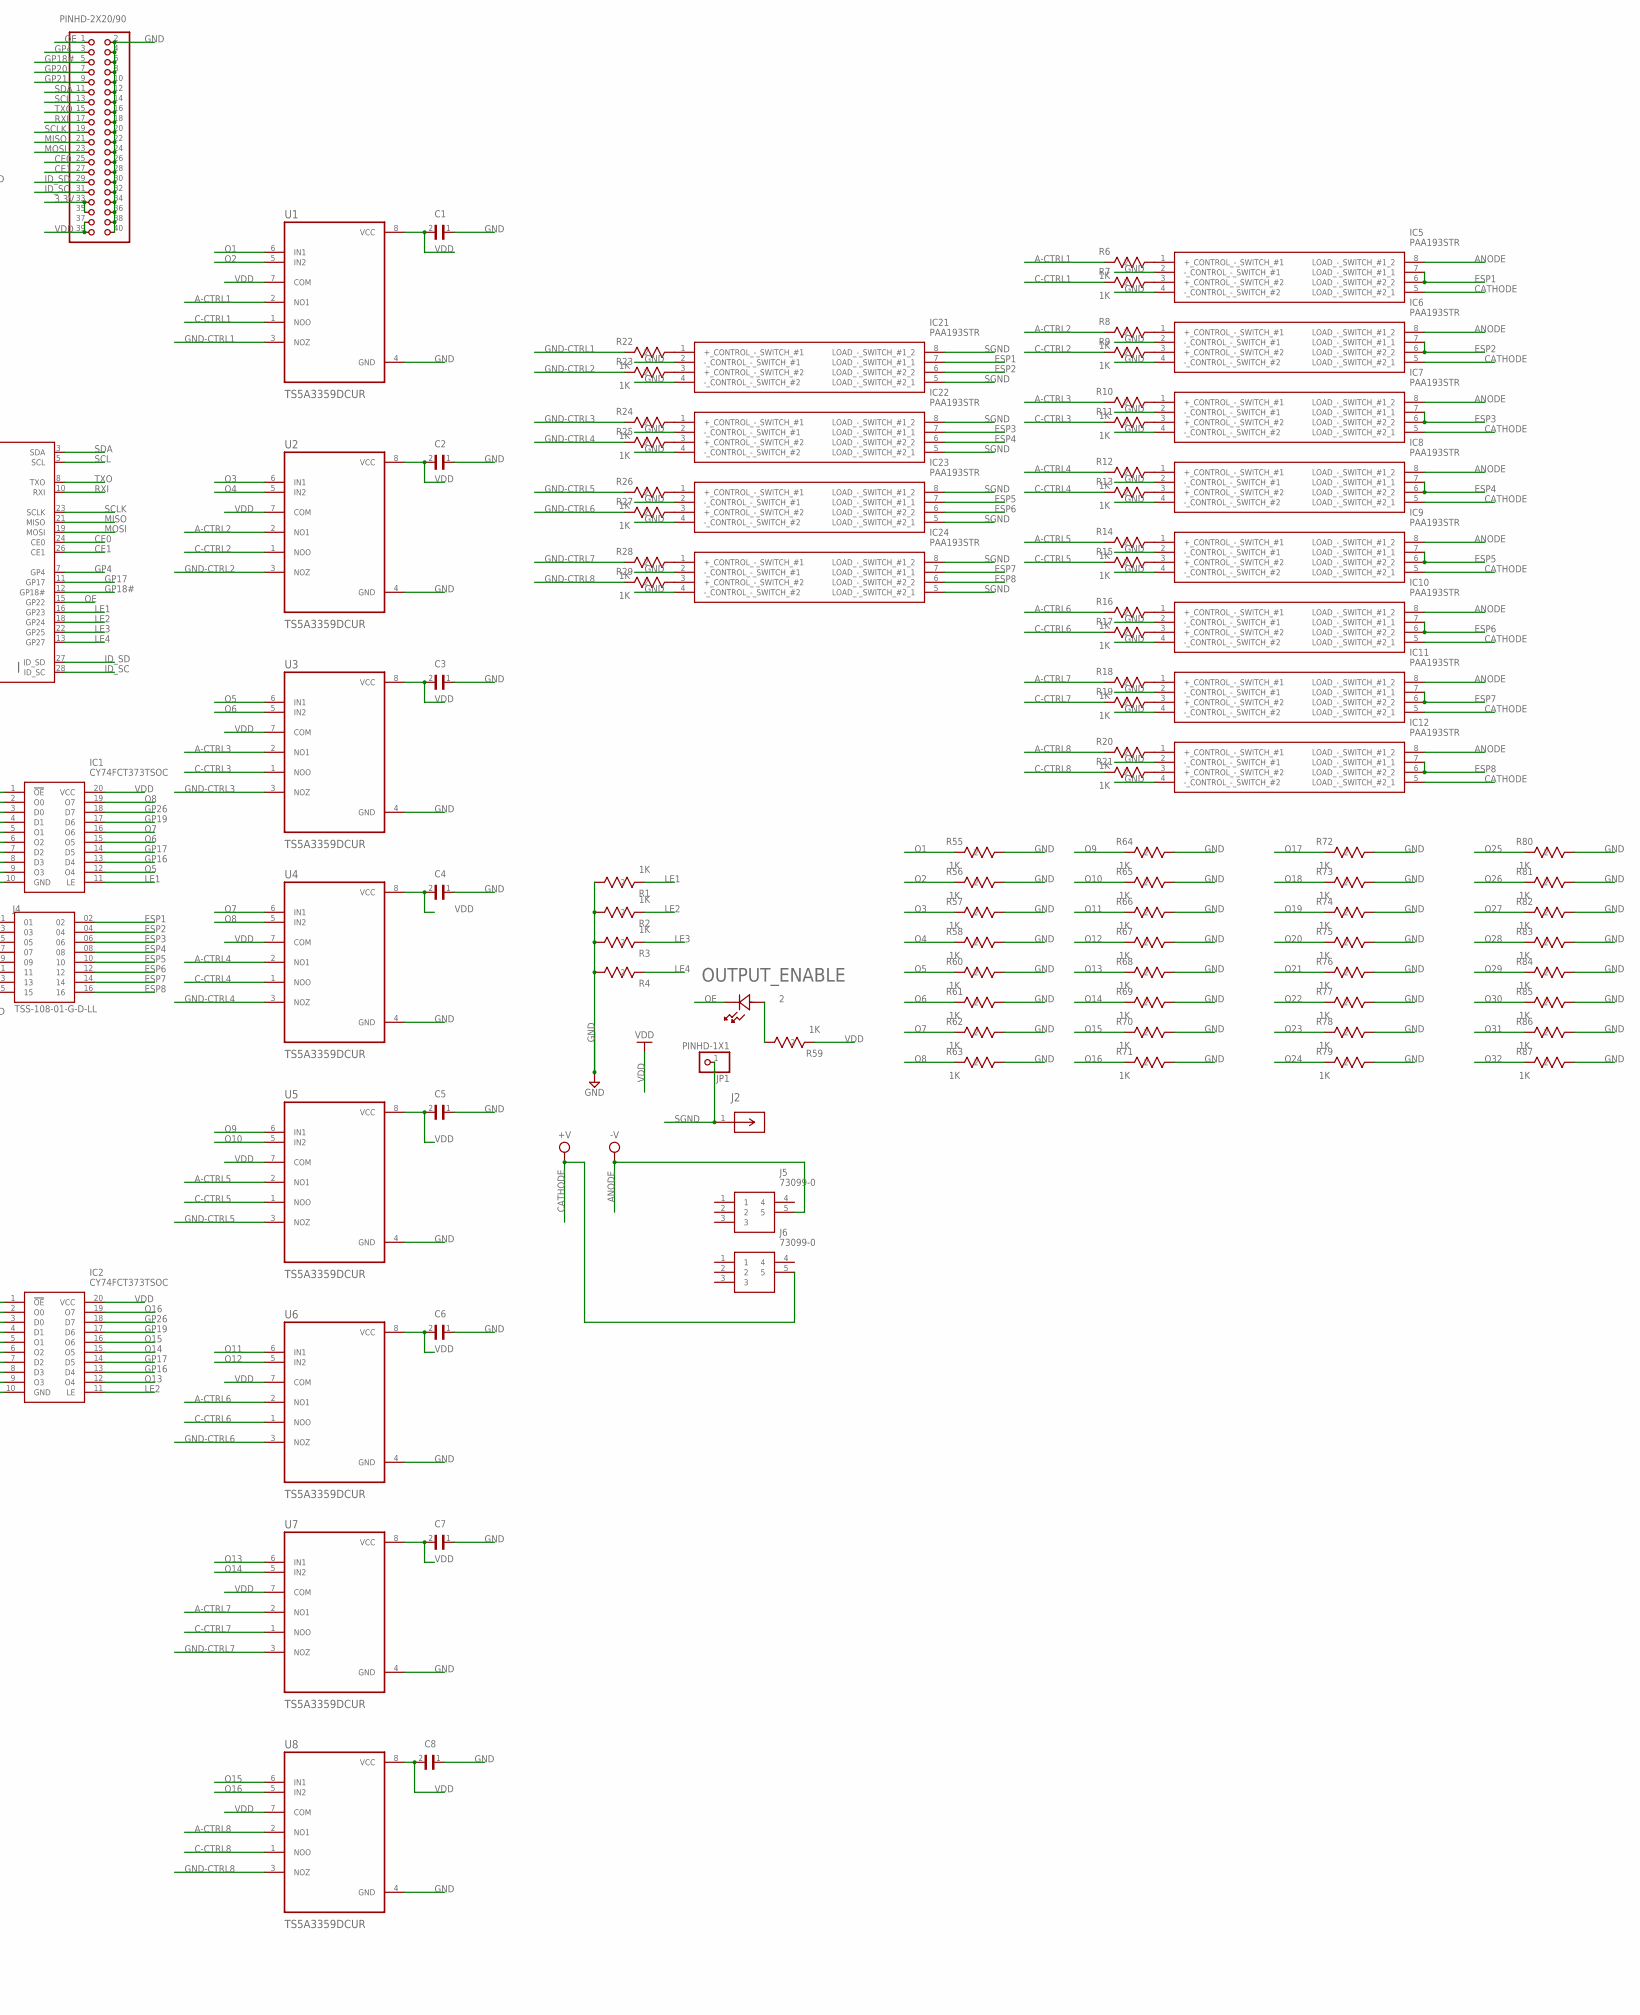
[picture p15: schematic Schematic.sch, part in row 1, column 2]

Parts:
C1, C2, C3, C4, C5, C6, C7, C8, C9, C10, C11, C12, C13, C14, C15, C16: CL05A104KA5NNNC; CAPC1005X55N
IC1, IC2, IC3, IC4: CY74FCT373TSOC; SOIC127P1030X265-20N
IC5, IC6, IC7, IC8, IC9, IC10, IC11, IC12, IC13, IC14, IC15, IC16, IC17, IC18, IC19, IC20, IC21, IC22, IC23, IC24, IC25, IC26, IC27, IC28: PAA193STR; SOP254P952X457-8N
J2: FCR7350GCONN_FCR7350G_CLF; CONN_FCR7350G_CLF
J3: RASPBERRYPI-40-PIN-GPIO_PTH_NO_SHROUD; 2X20
J4, J7: TSS-108-01-G-D-LL; SAMTEC_TSS-108-01-G-D-LL
J5, J6: 73099-0; 730990
JP1: PINHD-1X1; 1X01
JP4: PINHD-2X20/90; 2X20/90
OUTPUT_ENABLE: LTST-C190GKTLED_LTST-C190CKT_LTO; LED_LTST-C190CKT_LTO
POWER: LTST-C190GKTLED_LTST-C190CKT_LTO; LED_LTST-C190CKT_LTO
R1, R2, R3, R6, R7, R8, R9, R10, R11, R12, R13, R14, R15, R16, R17, R18, R19, R20, R21, R22, R23, R24, R25, R26, R27, R28, R29, R30, R31, R32, R33, R34, R35, R36, R37, R38, R39, R40, R41, R42, R43, R44, R45, R46, R47, R48, R49, R50, R51, R52, R53, R54, R55, R56, R57, R58, R59, R60, R61, R62, R63, R64, R65, R66, R67, R68, R69, R70, R71, R72, R73, R74, R75, R76, R77, R78, R79, R80, R81, R82, R83, R84, R85, R86, R87: 1K; RC0402N_YAG
R4: RC0402JR-071KLRC0402N_YAG; RC0402N_YAG
U1, U2, U3, U4, U5, U6, U7, U8, U9, U10, U11, U12, U13, U14, U15, U16: TS5A3359DCUR; SOP50P310X90-8N

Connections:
2: OUTPUT_ENABLE.2, R59.1
3.3V: J3.1 (3.3V), J3.17 (3.3V), JP4.33, JP4.35
A-CTRL1: R6.2, U1.2 (NO1)
A-CTRL2: R8.2, U2.2 (NO1)
A-CTRL3: R10.2, U3.2 (NO1)
A-CTRL4: R12.2, U4.2 (NO1)
A-CTRL5: R14.2, U5.2 (NO1)
A-CTRL6: R16.2, U6.2 (NO1)
A-CTRL7: R18.2, U7.2 (NO1)
A-CTRL8: R20.2, U8.2 (NO1)
A-CTRL9: R38.2, U9.2 (NO1)
A-CTRL10: R40.2, U10.2 (NO1)
A-CTRL11: R42.2, U11.2 (NO1)
A-CTRL12: R44.2, U12.2 (NO1)
A-CTRL13: R46.2, U13.2 (NO1)
A-CTRL14: R48.2, U14.2 (NO1)
A-CTRL15: R50.2, U15.2 (NO1)
A-CTRL16: R52.2, U16.2 (NO1)
ANODE: IC5.8 (LOAD_-_SWITCH_#1_2), IC6.8 (LOAD_-_SWITCH_#1_2), IC7.8 (LOAD_-_SWITCH_#1_2), IC8.8 (LOAD_-_SWITCH_#1_2), IC9.8 (LOAD_-_SWITCH_#1_2), IC10.8 (LOAD_-_SWITCH_#1_2), IC11.8 (LOAD_-_SWITCH_#1_2), IC12.8 (LOAD_-_SWITCH_#1_2), IC13.8 (LOAD_-_SWITCH_#1_2), IC14.8 (LOAD_-_SWITCH_#1_2), IC15.8 (LOAD_-_SWITCH_#1_2), IC16.8 (LOAD_-_SWITCH_#1_2), IC17.8 (LOAD_-_SWITCH_#1_2), IC18.8 (LOAD_-_SWITCH_#1_2), IC19.8 (LOAD_-_SWITCH_#1_2), IC20.8 (LOAD_-_SWITCH_#1_2), J5.5
C-CTRL1: R7.2, U1.1 (NOO)
C-CTRL2: R9.2, U2.1 (NOO)
C-CTRL3: R11.2, U3.1 (NOO)
C-CTRL4: R13.2, U4.1 (NOO)
C-CTRL5: R15.2, U5.1 (NOO)
C-CTRL6: R17.2, U6.1 (NOO)
C-CTRL7: R19.2, U7.1 (NOO)
C-CTRL8: R21.2, U8.1 (NOO)
C-CTRL9: R39.2, U9.1 (NOO)
C-CTRL10: R41.2, U10.1 (NOO)
C-CTRL11: R43.2, U11.1 (NOO)
C-CTRL12: R45.2, U12.1 (NOO)
C-CTRL13: R47.2, U13.1 (NOO)
C-CTRL14: R49.2, U14.1 (NOO)
C-CTRL15: R51.2, U15.1 (NOO)
C-CTRL16: R53.2, U16.1 (NOO)
CATHODE: IC5.5 (LOAD_-_SWITCH_#2_1), IC6.5 (LOAD_-_SWITCH_#2_1), IC7.5 (LOAD_-_SWITCH_#2_1), IC8.5 (LOAD_-_SWITCH_#2_1), IC9.5 (LOAD_-_SWITCH_#2_1), IC10.5 (LOAD_-_SWITCH_#2_1), IC11.5 (LOAD_-_SWITCH_#2_1), IC12.5 (LOAD_-_SWITCH_#2_1), IC13.5 (LOAD_-_SWITCH_#2_1), IC14.5 (LOAD_-_SWITCH_#2_1), IC15.5 (LOAD_-_SWITCH_#2_1), IC16.5 (LOAD_-_SWITCH_#2_1), IC17.5 (LOAD_-_SWITCH_#2_1), IC18.5 (LOAD_-_SWITCH_#2_1), IC19.5 (LOAD_-_SWITCH_#2_1), IC20.5 (LOAD_-_SWITCH_#2_1), J6.5
CE0: J3.24 (CE0), JP4.25
CE1: J3.26 (CE1), JP4.27
ESP1: IC5.6 (LOAD_-_SWITCH_#2_2), IC5.7 (LOAD_-_SWITCH_#1_1), IC21.7 (LOAD_-_SWITCH_#1_1), J4.02
ESP2: IC6.6 (LOAD_-_SWITCH_#2_2), IC6.7 (LOAD_-_SWITCH_#1_1), IC21.6 (LOAD_-_SWITCH_#2_2), J4.04
ESP3: IC7.6 (LOAD_-_SWITCH_#2_2), IC7.7 (LOAD_-_SWITCH_#1_1), IC22.7 (LOAD_-_SWITCH_#1_1), J4.06
ESP4: IC8.6 (LOAD_-_SWITCH_#2_2), IC8.7 (LOAD_-_SWITCH_#1_1), IC22.6 (LOAD_-_SWITCH_#2_2), J4.08
ESP5: IC9.6 (LOAD_-_SWITCH_#2_2), IC9.7 (LOAD_-_SWITCH_#1_1), IC23.7 (LOAD_-_SWITCH_#1_1), J4.10
ESP6: IC10.6 (LOAD_-_SWITCH_#2_2), IC10.7 (LOAD_-_SWITCH_#1_1), IC23.6 (LOAD_-_SWITCH_#2_2), J4.12
ESP7: IC11.6 (LOAD_-_SWITCH_#2_2), IC11.7 (LOAD_-_SWITCH_#1_1), IC24.7 (LOAD_-_SWITCH_#1_1), J4.14
ESP8: IC12.6 (LOAD_-_SWITCH_#2_2), IC12.7 (LOAD_-_SWITCH_#1_1), IC24.6 (LOAD_-_SWITCH_#2_2), J4.16
ESP9: IC13.6 (LOAD_-_SWITCH_#2_2), IC13.7 (LOAD_-_SWITCH_#1_1), IC25.7 (LOAD_-_SWITCH_#1_1), J7.02
ESP10: IC14.6 (LOAD_-_SWITCH_#2_2), IC14.7 (LOAD_-_SWITCH_#1_1), IC25.6 (LOAD_-_SWITCH_#2_2), J7.04
ESP11: IC15.6 (LOAD_-_SWITCH_#2_2), IC15.7 (LOAD_-_SWITCH_#1_1), IC26.7 (LOAD_-_SWITCH_#1_1), J7.06
ESP12: IC16.6 (LOAD_-_SWITCH_#2_2), IC16.7 (LOAD_-_SWITCH_#1_1), IC26.6 (LOAD_-_SWITCH_#2_2), J7.08
ESP13: IC17.6 (LOAD_-_SWITCH_#2_2), IC17.7 (LOAD_-_SWITCH_#1_1), IC27.7 (LOAD_-_SWITCH_#1_1), J7.10
ESP14: IC18.6 (LOAD_-_SWITCH_#2_2), IC18.7 (LOAD_-_SWITCH_#1_1), IC27.6 (LOAD_-_SWITCH_#2_2), J7.12
ESP15: IC19.6 (LOAD_-_SWITCH_#2_2), IC19.7 (LOAD_-_SWITCH_#1_1), IC28.7 (LOAD_-_SWITCH_#1_1), J7.14
ESP16: IC20.6 (LOAD_-_SWITCH_#2_2), IC20.7 (LOAD_-_SWITCH_#1_1), IC28.6 (LOAD_-_SWITCH_#2_2), J7.16
GND: C1.1, C2.1, C3.1, C4.1, C5.1, C6.1, C7.1, C8.1, C9.1, C10.1, C11.1, C12.1, C13.1, C14.1, C15.1, C16.1, IC1.10 (GND), IC2.10 (GND), IC3.10 (GND), IC4.10 (GND), IC5.2 (-_CONTROL_-_SWITCH_#1), IC5.4 (-_CONTROL_-_SWITCH_#2), IC6.2 (-_CONTROL_-_SWITCH_#1), IC6.4 (-_CONTROL_-_SWITCH_#2), IC7.2 (-_CONTROL_-_SWITCH_#1), IC7.4 (-_CONTROL_-_SWITCH_#2), IC8.2 (-_CONTROL_-_SWITCH_#1), IC8.4 (-_CONTROL_-_SWITCH_#2), IC9.2 (-_CONTROL_-_SWITCH_#1), IC9.4 (-_CONTROL_-_SWITCH_#2), IC10.2 (-_CONTROL_-_SWITCH_#1), IC10.4 (-_CONTROL_-_SWITCH_#2), IC11.2 (-_CONTROL_-_SWITCH_#1), IC11.4 (-_CONTROL_-_SWITCH_#2), IC12.2 (-_CONTROL_-_SWITCH_#1), IC12.4 (-_CONTROL_-_SWITCH_#2), IC13.2 (-_CONTROL_-_SWITCH_#1), IC13.4 (-_CONTROL_-_SWITCH_#2), IC14.2 (-_CONTROL_-_SWITCH_#1), IC14.4 (-_CONTROL_-_SWITCH_#2), IC15.2 (-_CONTROL_-_SWITCH_#1), IC15.4 (-_CONTROL_-_SWITCH_#2), IC16.2 (-_CONTROL_-_SWITCH_#1), IC16.4 (-_CONTROL_-_SWITCH_#2), IC17.2 (-_CONTROL_-_SWITCH_#1), IC17.4 (-_CONTROL_-_SWITCH_#2), IC18.2 (-_CONTROL_-_SWITCH_#1), IC18.4 (-_CONTROL_-_SWITCH_#2), IC19.2 (-_CONTROL_-_SWITCH_#1), IC19.4 (-_CONTROL_-_SWITCH_#2), IC20.2 (-_CONTROL_-_SWITCH_#1), IC20.4 (-_CONTROL_-_SWITCH_#2), IC21.2 (-_CONTROL_-_SWITCH_#1), IC21.4 (-_CONTROL_-_SWITCH_#2), IC22.2 (-_CONTROL_-_SWITCH_#1), IC22.4 (-_CONTROL_-_SWITCH_#2), IC23.2 (-_CONTROL_-_SWITCH_#1), IC23.4 (-_CONTROL_-_SWITCH_#2), IC24.2 (-_CONTROL_-_SWITCH_#1), IC24.4 (-_CONTROL_-_SWITCH_#2), IC25.2 (-_CONTROL_-_SWITCH_#1), IC25.4 (-_CONTROL_-_SWITCH_#2), IC26.2 (-_CONTROL_-_SWITCH_#1), IC26.4 (-_CONTROL_-_SWITCH_#2), IC27.2 (-_CONTROL_-_SWITCH_#1), IC27.4 (-_CONTROL_-_SWITCH_#2), IC28.2 (-_CONTROL_-_SWITCH_#1), IC28.4 (-_CONTROL_-_SWITCH_#2), J3.6 (GND), J3.9 (GND), J3.14 (GND), J3.20 (GND), J3.25 (GND), J3.30 (GND), J3.34 (GND), J3.39 (GND), J4.01, J4.03, J4.05, J4.07, J4.09, J4.11, J4.13, J4.15, J7.01, J7.03, J7.05, J7.07, J7.09, J7.11, J7.13, J7.15, JP4.2, JP4.4, JP4.6, JP4.8, JP4.10, JP4.12, JP4.14, JP4.16, JP4.18, JP4.20, JP4.22, JP4.24, JP4.26, JP4.28, JP4.30, JP4.32, JP4.34, JP4.36, JP4.38, JP4.40, POWER.1, R1.1, R2.1, R3.1, R4.1, R55.1, R56.1, R57.1, R58.1, R60.1, R61.1, R62.1, R63.1, R64.1, R65.1, R66.1, R67.1, R68.1, R69.1, R70.1, R71.1, R72.1, R73.1, R74.1, R75.1, R76.1, R77.1, R78.1, R79.1, R80.1, R81.1, R82.1, R83.1, R84.1, R85.1, R86.1, R87.1, U1.4 (GND), U2.4 (GND), U3.4 (GND), U4.4 (GND), U5.4 (GND), U6.4 (GND), U7.4 (GND), U8.4 (GND), U9.4 (GND), U10.4 (GND), U11.4 (GND), U12.4 (GND), U13.4 (GND), U14.4 (GND), U15.4 (GND), U16.4 (GND)
GND-CTRL1: R22.2, U1.3 (NOZ)
GND-CTRL2: R23.2, U2.3 (NOZ)
GND-CTRL3: R24.2, U3.3 (NOZ)
GND-CTRL4: R25.2, U4.3 (NOZ)
GND-CTRL5: R26.2, U5.3 (NOZ)
GND-CTRL6: R27.2, U6.3 (NOZ)
GND-CTRL7: R28.2, U7.3 (NOZ)
GND-CTRL8: R29.2, U8.3 (NOZ)
GND-CTRL9: R30.2, U9.3 (NOZ)
GND-CTRL10: R31.2, U10.3 (NOZ)
GND-CTRL11: R32.2, U11.3 (NOZ)
GND-CTRL12: R33.2, U12.3 (NOZ)
GND-CTRL13: R34.2, U13.3 (NOZ)
GND-CTRL14: R35.2, U14.3 (NOZ)
GND-CTRL15: R36.2, U15.3 (NOZ)
GND-CTRL16: R37.2, U16.3 (NOZ)
GP4: J3.7 (GP4), JP4.3
GP5: IC1.3 (D0), IC2.3 (D0), IC3.3 (D0), IC4.3 (D0), J3.29 (GP5)
GP6: IC1.4 (D1), IC2.4 (D1), IC3.4 (D1), IC4.4 (D1), J3.31 (GP6)
GP12: IC1.7 (D2), IC2.7 (D2), IC3.7 (D2), IC4.7 (D2), J3.32 (GP12)
GP13: IC1.8 (D3), IC2.8 (D3), IC3.8 (D3), IC4.8 (D3), J3.33 (GP13)
GP16: IC1.13 (D4), IC2.13 (D4), IC3.13 (D4), IC4.13 (D4), J3.36 (GP16)
GP17: IC1.14 (D5), IC2.14 (D5), IC3.14 (D5), IC4.14 (D5), J3.11 (GP17)
GP18#: J3.12 (GP18#), JP4.5
GP19: IC1.17 (D6), IC2.17 (D6), IC3.17 (D6), IC4.17 (D6), J3.35 (GP19)
GP20: J3.38 (GP20), JP4.7
GP21: J3.40 (GP21), JP4.9
GP26: IC1.18 (D7), IC2.18 (D7), IC3.18 (D7), IC4.18 (D7), J3.37 (GP26)
ID_SC: J3.28 (ID_SC), JP4.31
ID_SD: J3.27 (ID_SD), JP4.29
LE1: IC1.11 (LE), J3.16 (GP23), R1.2
LE2: IC2.11 (LE), J3.18 (GP24), R2.2
LE3: IC3.11 (LE), J3.22 (GP25), R3.2
LE4: IC4.11 (LE), J3.13 (GP27), R4.2
MISO: J3.21 (MISO), JP4.21
MOSI: J3.19 (MOSI), JP4.23
unnamed: POWER.2, R54.2
unnamed: IC5.1 (+_CONTROL_-_SWITCH_#1), R6.1
unnamed: IC5.3 (+_CONTROL_-_SWITCH_#2), R7.1
unnamed: IC6.1 (+_CONTROL_-_SWITCH_#1), R8.1
unnamed: IC6.3 (+_CONTROL_-_SWITCH_#2), R9.1
unnamed: IC7.1 (+_CONTROL_-_SWITCH_#1), R10.1
unnamed: IC7.3 (+_CONTROL_-_SWITCH_#2), R11.1
unnamed: IC8.1 (+_CONTROL_-_SWITCH_#1), R12.1
unnamed: IC8.3 (+_CONTROL_-_SWITCH_#2), R13.1
unnamed: IC9.1 (+_CONTROL_-_SWITCH_#1), R14.1
unnamed: IC9.3 (+_CONTROL_-_SWITCH_#2), R15.1
unnamed: IC10.1 (+_CONTROL_-_SWITCH_#1), R16.1
unnamed: IC10.3 (+_CONTROL_-_SWITCH_#2), R17.1
unnamed: IC11.1 (+_CONTROL_-_SWITCH_#1), R18.1
unnamed: IC11.3 (+_CONTROL_-_SWITCH_#2), R19.1
unnamed: IC12.1 (+_CONTROL_-_SWITCH_#1), R20.1
unnamed: IC12.3 (+_CONTROL_-_SWITCH_#2), R21.1
unnamed: IC21.1 (+_CONTROL_-_SWITCH_#1), R22.1
unnamed: IC21.3 (+_CONTROL_-_SWITCH_#2), R23.1
unnamed: IC22.1 (+_CONTROL_-_SWITCH_#1), R24.1
unnamed: IC22.3 (+_CONTROL_-_SWITCH_#2), R25.1
unnamed: IC23.1 (+_CONTROL_-_SWITCH_#1), R26.1
unnamed: IC23.3 (+_CONTROL_-_SWITCH_#2), R27.1
unnamed: IC24.1 (+_CONTROL_-_SWITCH_#1), R28.1
unnamed: IC24.3 (+_CONTROL_-_SWITCH_#2), R29.1
unnamed: IC25.1 (+_CONTROL_-_SWITCH_#1), R30.1
unnamed: IC25.3 (+_CONTROL_-_SWITCH_#2), R31.1
unnamed: IC26.1 (+_CONTROL_-_SWITCH_#1), R32.1
unnamed: IC26.3 (+_CONTROL_-_SWITCH_#2), R33.1
unnamed: IC27.1 (+_CONTROL_-_SWITCH_#1), R34.1
unnamed: IC27.3 (+_CONTROL_-_SWITCH_#2), R35.1
unnamed: IC28.1 (+_CONTROL_-_SWITCH_#1), R36.1
unnamed: IC28.3 (+_CONTROL_-_SWITCH_#2), R37.1
unnamed: IC13.1 (+_CONTROL_-_SWITCH_#1), R38.1
unnamed: IC13.3 (+_CONTROL_-_SWITCH_#2), R39.1
unnamed: IC14.1 (+_CONTROL_-_SWITCH_#1), R40.1
unnamed: IC14.3 (+_CONTROL_-_SWITCH_#2), R41.1
unnamed: IC15.1 (+_CONTROL_-_SWITCH_#1), R42.1
unnamed: IC15.3 (+_CONTROL_-_SWITCH_#2), R43.1
unnamed: IC16.1 (+_CONTROL_-_SWITCH_#1), R44.1
unnamed: IC16.3 (+_CONTROL_-_SWITCH_#2), R45.1
unnamed: IC17.1 (+_CONTROL_-_SWITCH_#1), R46.1
unnamed: IC17.3 (+_CONTROL_-_SWITCH_#2), R47.1
unnamed: IC18.1 (+_CONTROL_-_SWITCH_#1), R48.1
unnamed: IC18.3 (+_CONTROL_-_SWITCH_#2), R49.1
unnamed: IC19.1 (+_CONTROL_-_SWITCH_#1), R50.1
unnamed: IC19.3 (+_CONTROL_-_SWITCH_#2), R51.1
unnamed: IC20.1 (+_CONTROL_-_SWITCH_#1), R52.1
unnamed: IC20.3 (+_CONTROL_-_SWITCH_#2), R53.1
O1: IC1.2 (O0), R55.2, U1.6 (IN1)
O2: IC1.5 (O1), R56.2, U1.5 (IN2)
O3: IC1.6 (O2), R57.2, U2.6 (IN1)
O4: IC1.9 (O3), R58.2, U2.5 (IN2)
O5: IC1.12 (O4), R60.2, U3.6 (IN1)
O6: IC1.15 (O5), R61.2, U3.5 (IN2)
O7: IC1.16 (O6), R62.2, U4.6 (IN1)
O8: IC1.19 (O7), R63.2, U4.5 (IN2)
O9: IC2.2 (O0), R64.2, U5.6 (IN1)
O10: IC2.5 (O1), R65.2, U5.5 (IN2)
O11: IC2.6 (O2), R66.2, U6.6 (IN1)
O12: IC2.9 (O3), R67.2, U6.5 (IN2)
O13: IC2.12 (O4), R68.2, U7.6 (IN1)
O14: IC2.15 (O5), R69.2, U7.5 (IN2)
O15: IC2.16 (O6), R70.2, U8.6 (IN1)
O16: IC2.19 (O7), R71.2, U8.5 (IN2)
O17: IC3.2 (O0), R72.2, U9.6 (IN1)
O18: IC3.5 (O1), R73.2, U9.5 (IN2)
O19: IC3.6 (O2), R74.2, U10.6 (IN1)
O20: IC3.9 (O3), R75.2, U10.5 (IN2)
O21: IC3.12 (O4), R76.2, U11.6 (IN1)
O22: IC3.15 (O5), R77.2, U11.5 (IN2)
O23: IC3.16 (O6), R78.2, U12.6 (IN1)
O24: IC3.19 (O7), R79.2, U12.5 (IN2)
O25: IC4.2 (O0), R80.2, U13.6 (IN1)
O26: IC4.5 (O1), R81.2, U13.5 (IN2)
O27: IC4.6 (O2), R82.2, U14.6 (IN1)
O28: IC4.9 (O3), R83.2, U14.5 (IN2)
O29: IC4.12 (O4), R84.2, U15.6 (IN1)
O30: IC4.15 (O5), R85.2, U15.5 (IN2)
O31: IC4.16 (O6), R86.2, U16.6 (IN1)
O32: IC4.19 (O7), R87.2, U16.5 (IN2)
OE: IC1.1 (!OE), IC2.1 (!OE), IC3.1 (!OE), IC4.1 (!OE), J3.15 (GP22), JP4.1, OUTPUT_ENABLE.1
RXI: J3.10 (RXI), JP4.17
SCL: J3.5 (SCL), JP4.13
SCLK: J3.23 (SCLK), JP4.19
SDA: J3.3 (SDA), JP4.11
SGND: IC21.5 (LOAD_-_SWITCH_#2_1), IC21.8 (LOAD_-_SWITCH_#1_2), IC22.5 (LOAD_-_SWITCH_#2_1), IC22.8 (LOAD_-_SWITCH_#1_2), IC23.5 (LOAD_-_SWITCH_#2_1), IC23.8 (LOAD_-_SWITCH_#1_2), IC24.5 (LOAD_-_SWITCH_#2_1), IC24.8 (LOAD_-_SWITCH_#1_2), IC25.5 (LOAD_-_SWITCH_#2_1), IC25.8 (LOAD_-_SWITCH_#1_2), IC26.5 (LOAD_-_SWITCH_#2_1), IC26.8 (LOAD_-_SWITCH_#1_2), IC27.5 (LOAD_-_SWITCH_#2_1), IC27.8 (LOAD_-_SWITCH_#1_2), IC28.5 (LOAD_-_SWITCH_#2_1), IC28.8 (LOAD_-_SWITCH_#1_2), J2.1, JP1.1
TXO: J3.8 (TXO), JP4.15
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

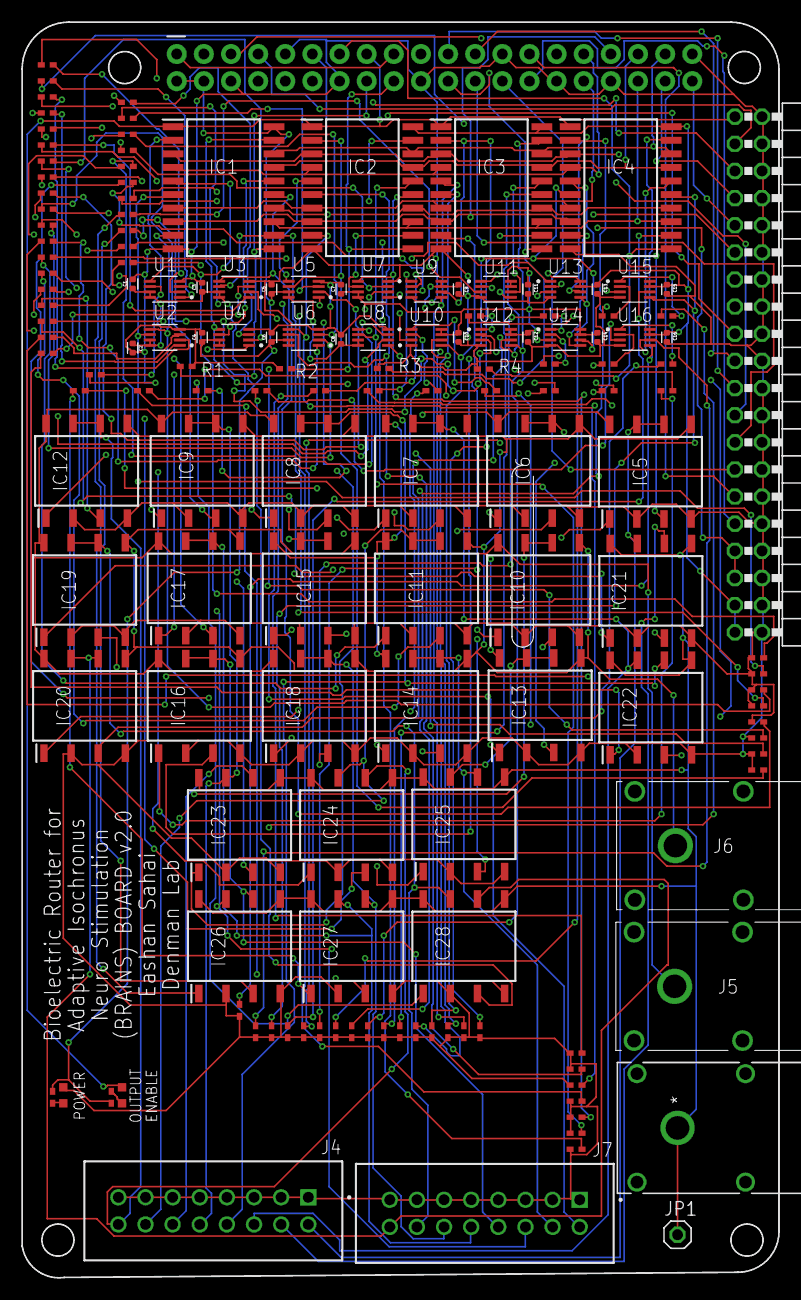
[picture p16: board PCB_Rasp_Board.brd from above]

Board: 4 copper layers, 70.8 x 117.5 mm, 156 parts (1 on the bottom side), 180 nets.

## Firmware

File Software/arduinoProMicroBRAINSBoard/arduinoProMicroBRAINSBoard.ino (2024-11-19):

#include <Arduino.h>

#define NUM_CHAN 16     //  Number of channels
#define NUM_LE    4     // Number of Latch Enables / Number of Channel Groups
#define NUM_CHAN_PER_GROUP  (NUM_CHAN/NUM_LE)
#define NUM_CONTROL  2  // Number of CONTROL pins per Channel Group
#define LE_0  1
#define LE_1  2
#define LE_2  3
#define LE_3  4
#define OE    16
#define CS_0  5
#define CS_1  (CS_0+1)
#define CS_2  (CS_0+2)
#define CS_3  (CS_0+3)
#define CS_4  (CS_0+4)
#define CS_5  (CS_0+5)
#define CS_6  (CS_0+9)
#define CS_7  (CS_0+10)


#define STATE_IDLE  0
#define STATE_GET_CHAN_NUM  1
#define STATE_GET_CHAN_VALUE  2
#define STATE_APPLY   3
#define STATE_ERROR   4
#define STATE_SET_DELAY 5
#define STATE_EXTERNAL_WAIT   6
#define STATE_EXECUTE_COMMAND 7
#define STATE_SET_LOOP   8
#define STATE_LOOP_EXECUTE 9

// Pin definitions
#define EXTERNAL_TRIGGER_PIN 18

long delayDuration = 0; // to store the delay duration
char delayUnit = 'u'; // default to microseconds
bool trig_started = false;

int loops_number = -1; // -1 indicates no looping by default
bool is_looping = false; // Whether looping is active
char commandHistory[1000];
int character_pos = 0;
int current_state = STATE_IDLE;

char channel_state[] = {'G','G','G','G','G','G','G','G','G','G','G','G','G','G','G','G'};
int le_state[NUM_LE] = {1, 1, 1, 1};
int le_gpio_pins[4] = {LE_0, LE_1, LE_2, LE_3} ; // Example GPIO pins, adjust as needed

struct Position {
    int x;
    int y;
};

Position map_value_to_logic(char value) {
    switch (value) {
        case 'F': return {0, 0};
        case 'C': return {1, 0};
        case 'A': return {0, 1};
        case 'G': return {1, 1};
        default:  return {-1, -1};
    }
}
int to_hex(char c) {
    switch (c) {
        case '2': return 0;
        case '4': return 1;
        case '6': return 2;
        case '3': return 3;
        case '7': return 4;
        case '5': return 5;
        case '1': return 6;
        case '8': return 7;
        case 'D': case 'd': return 8;
        case 'G': case 'g': return 9;
        case 'E': case 'e': return 10; // A in hex
        case 'F': case 'f': return 11; // B in hex
        case 'B': case 'b': return 12; // C in hex
        case '9': return 13;           // D in hex
        case 'A': case 'a': return 14; // E in hex
        case 'C': case 'c': return 15; // F in hex
        default: return -1; // Invalid character
    }
}
int sp3t_selector_gpio_pins[NUM_LE][NUM_CONTROL] = {
    {CS_0, CS_1}, // Pins for channel group 0
    {CS_2, CS_3}, // Pins for channel group 1
    {CS_4, CS_5}, // Pins for channel group 2
    {CS_6, CS_7} // Pins for channel group 3
};

int is_channel_value(char c) {
    switch(c) {
      case 'A':
      case 'C':
      case 'F':
      case 'G':
      case 'a':
      case 'c':
      case 'f':
      case 'g':
        return 1;
      default:
        return 0;
    }
}

void set_channel_state(int channel, Position pos) {
    int group = floor(channel / 4);
    int channelWithinGroup = channel % 4;
    int x = sp3t_selector_gpio_pins[channelWithinGroup][0];
    int y = sp3t_selector_gpio_pins[channelWithinGroup][1];

    digitalWrite(x, pos.x);
    digitalWrite(y, pos.y);
    //Serial.print("Setting Pin ");
    //Serial.print(x);
    //Serial.print(" to ");
    ////Serial.println(pos.x);
    ////Serial.print("and Setting Pin ");
    ////Serial.print(y);
    ////Serial.print(" to ");
    ////Serial.println(pos.y);
}

void setup_and_latch(int gn) {
   

    for (int channel = gn*NUM_CHAN_PER_GROUP; channel < gn*NUM_CHAN_PER_GROUP + NUM_CHAN_PER_GROUP; channel++) {
        Position pos = map_value_to_logic(channel_state[channel]);
        set_channel_state(channel, pos);
    }
     // Activate and deactivate LE pin for the group with precise timing
     //Serial.print("Toggling LE pin: ");
     //Serial.println(le_gpio_pins[gn]);
    digitalWrite(le_gpio_pins[gn], HIGH);
    delayMicroseconds(3);
    digitalWrite(le_gpio_pins[gn], LOW);
}

void setup() {
    Serial.begin(115200);
    while (!Serial) continue; // Wait for Serial port to connect
    for (int i = LE_0; i <= LE_3; ++i) { // Setup LE pins as output
        pinMode(i, OUTPUT);
    }
    for (int i = CS_0; i <= CS_7; ++i) { // Setup CS pins as output
        pinMode(i, OUTPUT);
    }
    pinMode(OE, OUTPUT); // Setup OE pin as output
    pinMode(EXTERNAL_TRIGGER_PIN, INPUT); // Setup external trigger pin as input
    for (int i = 0; i < 50; i++) {
        commandHistory[i] = 0;
    }
    apply();
}

int get_char() {
  if (Serial.available() > 0) {
    char ch = Serial.read();
    //Serial.print("GOT: ");
    //Serial.println(ch);
    commandHistory[character_pos] = ch;
    character_pos++;
    //Serial.print("Command History: ");
    //Serial.println(commandHistory);
    return ch;
  } else if (is_looping == true)
  {
    //Serial.println(character_pos);
    char ch = commandHistory[character_pos];
    //Serial.print("GOT: ");
    //Serial.println(ch);
    //Serial.println(commandHistory);
    character_pos++;
    return ch;
  }
}

void print_current_state() {
  Serial.print( "[CS=>");
  for (int i=0; i < NUM_CHAN; i++) {
    Serial.print(channel_state[i]);
  }
  Serial.println("]\n");
}

void set_channel_value(int n, char v) {
  channel_state[n] = v;
  int gn = n / NUM_LE;
  le_state[gn] = 1;
}

void apply() {
  digitalWrite(OE, HIGH); // Disable output
  
  for (int gn = 0; gn < NUM_LE; gn++) {
    if (le_state[gn] == 0)
      continue;
    // Program the CS and toggle LE and reset LE to 0
    setup_and_latch(gn);
    le_state[gn] = 0;
  }
  digitalWrite(OE, LOW); // Enable output
  print_current_state();
}


void loop()
{
static char c = '\0';  // Initialize with a non-numeric and non-control value
static int current_chan_num;

//Serial.print(current_state);

switch (current_state) {
  case STATE_IDLE:
  {
    //Serial.println("State Idle");
    c = get_char();
    if (c == 'l') {
        //Serial.println("Loop command detected.");
        current_state = STATE_SET_LOOP;
    }
    else if (c == -1)
      break;
    else if (c == 'x') {
      //Serial.println("External Trigger Delay Beginning!");
      current_state = STATE_EXTERNAL_WAIT;
      break;
    } else if (c == '[') {
      //Serial.println("Reading!");
      current_state = STATE_GET_CHAN_NUM;
      break;
    } else if (c == '.') {
      //Serial.println("Reading!");
      current_state = STATE_IDLE;
      break;
    } else if (c == -1)
        trig_started = true;
        break; // No data available
    break;
  }
  case STATE_GET_CHAN_NUM:
  {
    //Serial.println("State Get Chan Num");
    c = get_char();
    if (c == -1) {
      Serial.println("Failed to get chan num");
      break;
    } else if (c == ']') {
      //Serial.println("Headed to apply from CHAN NUM!");
      current_state = STATE_APPLY;
      break;
    } else {
      current_chan_num = to_hex(c);
      //Serial.println(current_chan_num);
      if (current_chan_num == -1) {
        //Serial.println("UH OH!");
        current_state = STATE_IDLE;
        break;
      } else {
        current_state = STATE_GET_CHAN_VALUE;
        break;
      }
    }
}
  case STATE_GET_CHAN_VALUE:
  {
    //Serial.println("State Get Chan Value");
    c = get_char();
    if (c == -1)
      break;
    else if (c == ']') {
      //Serial.println("Headed to Apply from CHAN VALUE");
      current_state = STATE_APPLY;
      break;
    }
    int tf = is_channel_value(c);
    if (tf == 0) {
      //Serial.println("Uh oh at is_channel_value");
      current_state = STATE_IDLE;
      break;
    } else {
      set_channel_value(current_chan_num, c);
      current_state = STATE_GET_CHAN_NUM;
      //Serial.println(c);
      break;
    }
  }
  case STATE_APPLY:
  {
    //Serial.println("State Apply");
    apply();
    delayDuration = 0; // Reset delay duration
    delayUnit = 'u'; // Reset to default microseconds
    c = '\0'; // IMPORTANT: Reset 'c' so the delay state can process new characters
    //Serial.println("While in apply, got: ");
    c = get_char();
    //Serial.println(c);
    if (isdigit(c) > 0 && isdigit(c) <= 9){
        //Serial.println(" Headed to set delay");
        current_state = STATE_SET_DELAY;
    } else if (c == 'x') {
        //Serial.println("External Trigger Delay Beginning!");
        current_state = STATE_EXTERNAL_WAIT;
    } else if (c == 'l'){
        //Serial.println("Loop command detected.");
        current_state = STATE_SET_LOOP;
    } else { 
        //Serial.println(" Headed to idle");
        current_state = STATE_IDLE; // Move to the new state to set delay
        }
    break;
  }
  case STATE_EXTERNAL_WAIT:
  {
      bool printed = false;
      while (digitalRead(EXTERNAL_TRIGGER_PIN) != HIGH) {
        if (trig_started == true){
          trig_started = false;
          current_state = STATE_IDLE;
          //delayMicroseconds(300);
          break;
        }
      }
      while (digitalRead(EXTERNAL_TRIGGER_PIN) == HIGH && trig_started == false){
          //Serial.println("External trigger received, waiting...");
          trig_started = true;
      }
      //if (message_sent == false) //Serial.println("Waiting for External Trigger to end");
      delayMicroseconds(1);
      break;
  }
  case STATE_SET_DELAY:
  {
    //Serial.println("State Set Delay");
    if (c == '\0') {
        c = get_char(); // Get the next character if we need to start processing delay
    }

    // If 'c' is not a digit and not a delay unit, reset the state machine
    if (c == '[') {
      // ... handle the case for '['
    } else if (c < '0' || c > '9') {
      // We received a non-digit, non-unit character, go back to idle
      current_state = STATE_IDLE;
    }

    if (c == -1)
        break; // No data available
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

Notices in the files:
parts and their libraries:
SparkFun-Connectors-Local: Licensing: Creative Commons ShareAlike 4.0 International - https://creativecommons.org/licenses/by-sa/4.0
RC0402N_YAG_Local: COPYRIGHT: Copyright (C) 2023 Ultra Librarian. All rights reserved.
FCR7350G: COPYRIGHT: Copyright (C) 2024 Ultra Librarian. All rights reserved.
